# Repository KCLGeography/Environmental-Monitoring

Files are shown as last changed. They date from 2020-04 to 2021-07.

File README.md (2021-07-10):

[][cc-by]

# Environmental-Monitoring
This repo contains the open-source environmental monitoring hardware designs detailed in our *Low-cost electronic sensors for environmental research: pitfalls and opportunities* paper. Designs are included in their individual folders:  
**1. [Basic versatile logger](https://github.com/KCLGeography/environmental-monitoring/tree/master/basic-logger)**  
**2. [Water table depth probe](https://github.com/KCLGeography/environmental-monitoring/tree/master/depth-probe)**  
**3. [Air quality logger](https://github.com/KCLGeography/environmental-monitoring/tree/master/air-quality)**  
**4. [Water quality logger](https://github.com/KCLGeography/environmental-monitoring/tree/master/water-quality)**  
**5. [Time-sequencing lake sediment trap](https://github.com/KCLGeography/environmental-monitoring/blob/master/lake-sediment)**  
**6. [High-frequency measurements of wind-blown sand](https://github.com/KCLGeography/environmental-monitoring/tree/master/Aeolean-sediment-measurer)**  

Schematics and build instructions for the **Freestation Automated Weather Stations** and other specific designs can be found at [www.freestation.org](http://www.freestation.org)

# License
This work is licensed under a [Creative Commons Attribution 4.0 International
License][cc-by] - any use of any material here requires attribution.

### Citation Information:
Chan, K., Schillereff, D., Baas, A., Chadwick, M., Main, B., Mulligan, M., O'Shea, F., Pearce, R., Smith, T.E., van Soesbergen, A., Tebbs, E. and Thompson, J., 2021. Low-cost electronic sensors for environmental research: pitfalls and opportunities. <em>Progress in Physical Geography: Earth and Environment</em> 45(3): 305-338. **[DOI:10.1177/0309133320956567](https://doi.org/10.1177/0309133320956567)**

[][cc-by]

[cc-by]: http://creativecommons.org/licenses/by/4.0/
[cc-by-image]: https://i.creativecommons.org/l/by/4.0/88x31.png
[cc-by-shield]: https://img.shields.io/badge/License-CC%20BY%204.0-lightgrey.svg

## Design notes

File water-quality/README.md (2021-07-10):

[][cc-by]

# Water Quality Logger
Open-source hardware design for the aquatic water quality logger.

## Instructions:
1. Read and confirm the declaration and license associated with these instructions.
2. Start by following the instructions to build and test the [Basic core logger page](https://github.com/KCLGeography/environmental-monitoring/tree/master/basic-logger).

### Adding the DO probe
3. Connect the wires connecting the Atlas Scientific DO probe (complete wiring diagram below).
4. Download the [example code for the Atlas Scientific DO probe](https://www.atlas-scientific.com/_files/code/ino_files/Arduino_UNO_DO_sample_code.zip).
5. Define rx and tx to be 7 and 8 respectively.
6. Upload the file and open the Serial Monitor.
7. Follow the [instructions here](https://www.instructables.com/id/Atlas-Scientific-EZO-DO-Calibration-Procedure/) to calibrate the DO probe.

### Adding the remaining sensors
8. Connect the remaining sensors, including the 5V supply circuitry.
9. Upload the [WaterQualityLogger.ino sketch](WaterQualityLogger.ino).
10. Wait for the reading to occur (every minute) and check that readings are valid in the serial monitor. Results will be in CSV format of Year, month, day, hour, minute, Conductivity voltage, calibrated conductivity (ms/cm), pressure voltage, calibrated temperature (°C), Dissolved Oxygen reading (mg/L).

### Calibrating the EC probe
11. Download and install the [DFRobot_EC Arduino Library](https://github.com/DFRobot/DFRobot_EC/archive/master.zip) within your Arduino IDE.
12. Upload the [ECProbeCalibration.ino](ECProbeCalibration.ino) sketch and follow the calibration instructions [here](https://wiki.dfrobot.com/Gravity__Analog_Electrical_Conductivity_Sensor___Meter_V2__K%3D1__SKU_DFR0300#target_3) noting that you should be using the amended calibration sketch you have already installed, and changing the Serial baud rate to 9600.

### Preparing the final sketch
13. Back in the [WaterQualityLogger.ino sketch](WaterQualityLogger.ino), set the "sleep_period" to a desirable time and reupload the sketch (note, the maximum period without more significant amendment to the sketch is 59 minutes).
14. Test that the logger is working properly before deploying.  

## Wiring diagram (adapted from Fritzing diagram)
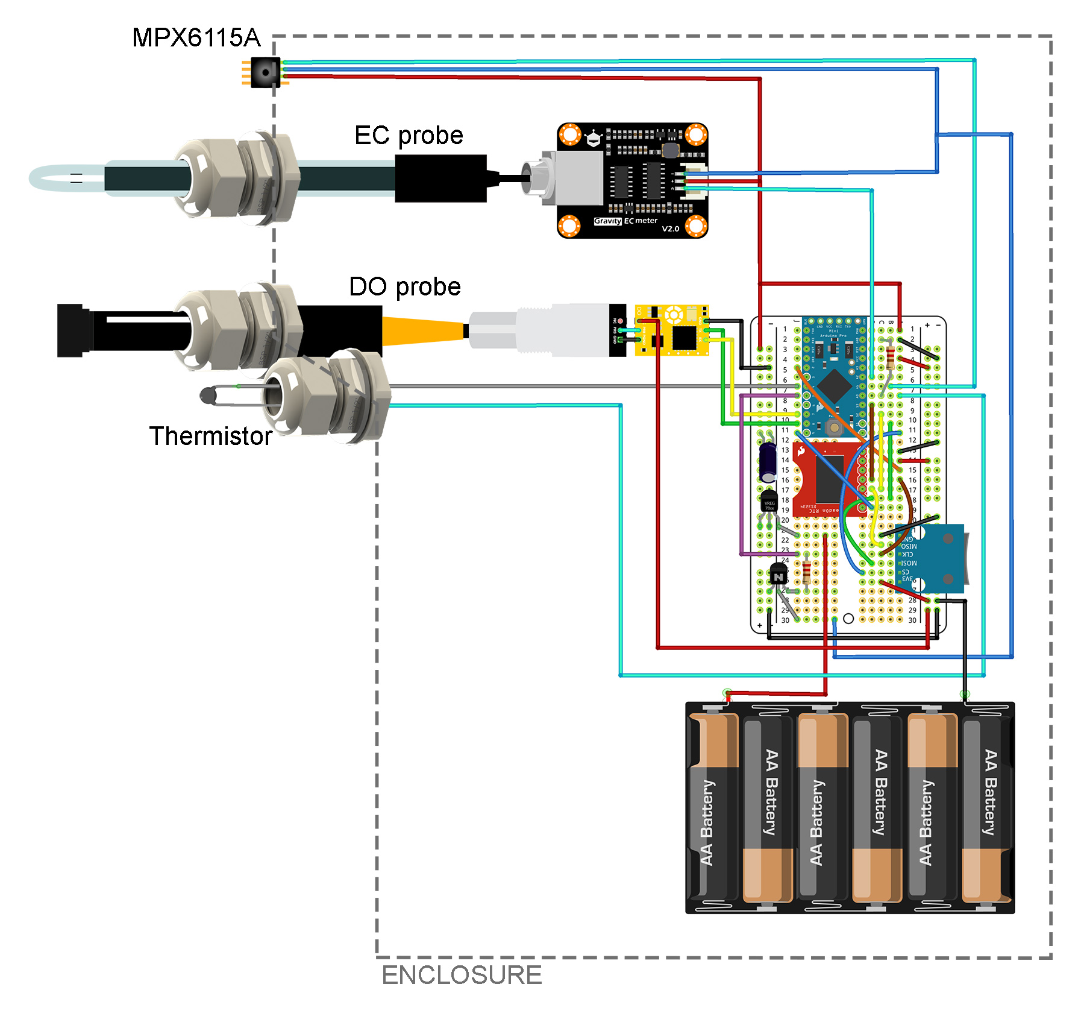
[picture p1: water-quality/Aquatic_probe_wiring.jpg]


## Disclaimer: 
The material in this repository is intended as documentation of the process by which the King's College London environmental monitoring team build our open-source loggers. Though we take care to ensure that the pages are accurate as of the date of publication, Arduino software, libraries, electronic components and interface devices are all subject to variation, change with time, and all introduce the potential for risk. The authors take no responsibility for the consequences of error or for any loss, damage or injury suffered by users or their property as a result of any of the information published on any of these pages, and such information does not form any basis of a contract with readers or users of it. The audience should verify any information provided and only proceed if they have an adequate understanding of electronics and electronics safety.

# License
This work is licensed under a [Creative Commons Attribution 4.0 International
License][cc-by] - any use of any material here requires attribution.

### Citation Information:
Chan, K., Schillereff, D., Baas, A., Chadwick, M., Main, B., Mulligan, M., O'Shea, F., Pearce, R., Smith, T.E., van Soesbergen, A., Tebbs, E. and Thompson, J., 2020. Low-cost electronic sensors for environmental research: pitfalls and opportunities. <em>Progress in Physical Geography: Earth and Environment</em> 45(3): 305-338. **[DOI:10.1177/0309133320956567](https://doi.org/10.1177/0309133320956567)**

[][cc-by]

[cc-by]: http://creativecommons.org/licenses/by/4.0/
[cc-by-image]: https://i.creativecommons.org/l/by/4.0/88x31.png
[cc-by-shield]: https://img.shields.io/badge/License-CC%20BY%204.0-lightgrey.svg

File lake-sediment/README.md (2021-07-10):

[][cc-by]

# Time-sequencing lake sediment traps
Open-source hardware design for time-sequencing lake sediment traps. in our design, the carousel rotates every month and exposes a new sediment trap, which collects sediment in the water column. 

## Instructions:
1. Read and confirm the declaration and license associated with these instructions.
2. Ensure you have purchased all the necessary parts listed in the [Bill of Materials sheet](https://docs.google.com/spreadsheets/d/1BAKtbqieHCemCTPPsL36uj2QXcKh0NGoTecxeYXc90M/edit#gid=1020050693).
3. In this design, we solder screw terminals to the components for more robust deployment, though direct soldering onto the components would be more secure. You can also adapt the instructions to using a breadboard. Start by assembling the basic logger by assembling the wiring diagram of the basic logger below.
4. Follow the test instructions on the [Basic core logger page](https://github.com/KCLGeography/environmental-monitoring/tree/master/basic-logger) to set and test the clock and microSD card communication.
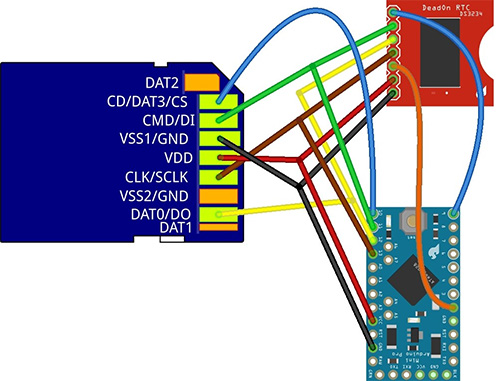
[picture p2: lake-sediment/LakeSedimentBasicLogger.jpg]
Soldered Basic Logger schematic (made with Fritzing)


### Adding the Relay
5. Add the Relay and communication ports for the stepper motor following the assembly diagram below or included in this folder: [LakeSedimentRelay.jpg](LakeSedimentRelay.jpg).
6. Upload the [LakeSedimentTrap sketch](LakeSedimentTrap.ino).
7. The stepper motor should rotate and the relay should click on/off. Though we could run the stepper without direct powering (i.e. without the need for the relay), it is more stable to run with this.
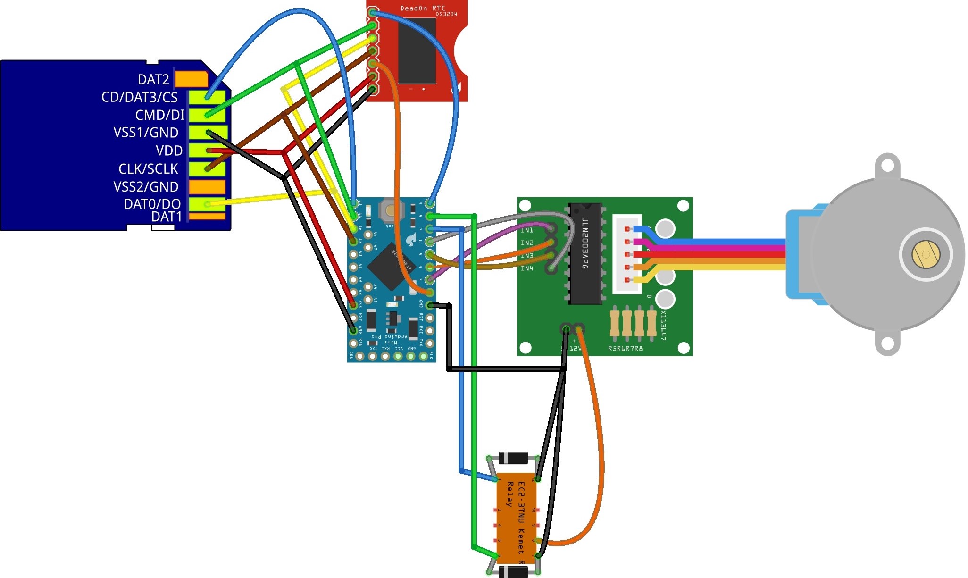
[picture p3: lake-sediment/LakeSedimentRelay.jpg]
Stepper and relay circuit schematic (made with Fritzing)


### Connecting the power pack
8. Connect the battery pack (6xAA recommended for annual deployment) following the wiring diagram below and test that the circuit still works.
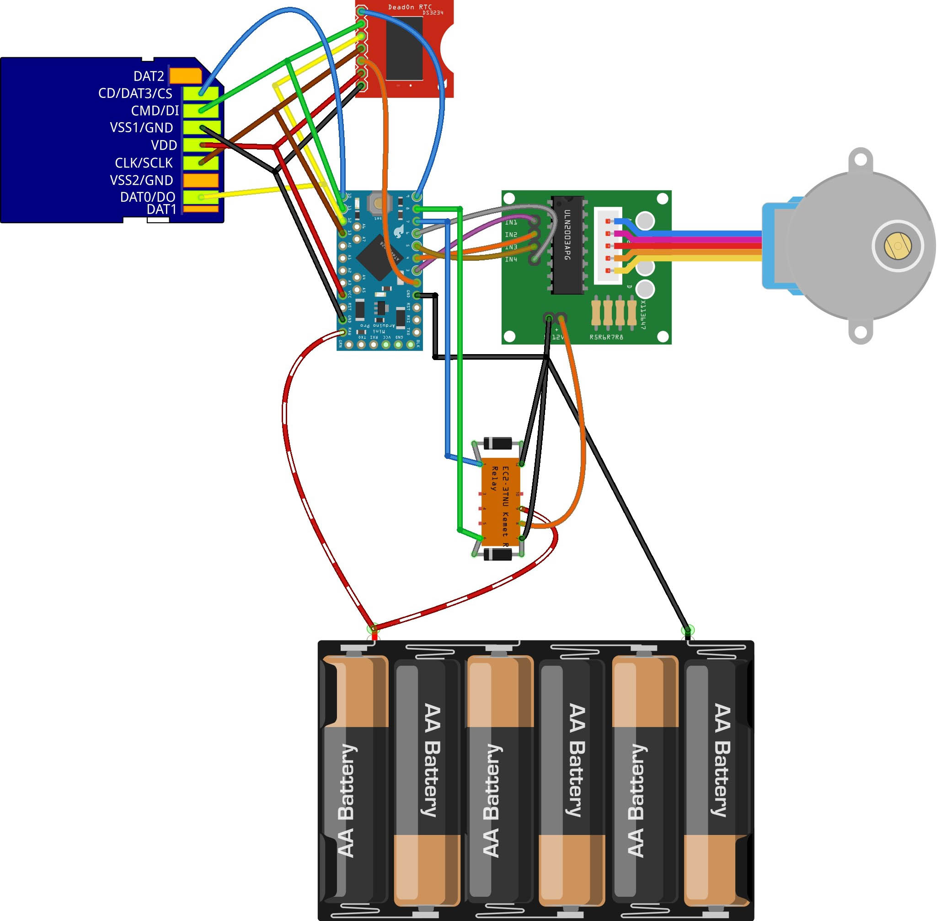
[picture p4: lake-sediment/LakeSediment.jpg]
Full circuit schematic (made with Fritzing)


## Assembling the hardware
Disconnect a battery whilst the below is prepared.

### Preparing the enclosure
9. Drill a 13mm hole in the center of a quadrant of the bottom of the enclosure. This is for the the cable gland and where the axle will pass through. Ensure that burrs on the edges are removed.
10. Check the fitting of the stepper, stepper mechanism and axle. If they fit together well, epoxy these together.
11. Mount the cable gland to the bottom of the enclosure and position the stepper motor in the correct position over the cable gland. Using epoxy, glue the mounting brackets for the stepper motor to the base of the enclosure. Also glue the enclosure to the top of the sediment trap cover.

### Preparing the carousel
12. Drill holes in the tops of 12 of the sampling bottles, being careful to remove and burrs.
13. With epoxy, glue the lids of the sampling bottles into the carousel.

### Preparing the trap top
14. Cut the filter such that it fits into the 4" pipe snugly.
15. Position the foam camping matt against the lake sediment trap top cover and cut around the trap cover. Mark and cut a small hole where the axle and filter will go through the piece - the holes should accommodate the axle and filter bottom snugly. 
16. Epoxy the prepared camping matt to the sediment trap top.
17. Cut the pipe to a length of 75cm.
18. Using epoxy, glue the filter and pipe to the top cover of the lake sediment trap. Wait for this to dry.
19. Put some silicon grease along the section of axle which will rotate within the gland.
20. Push the stepper and axle through the enclosure and mount the stepper motor to the brackets with nuts and bolts. Glue the axle as far through the sediment trap top as it will go whilst still mounted to the stepper in the correct position. The top of the carousel should be snug against the foam.
21. Wait for this to dry then test that it still works.

### Waterproofing
22. Apply silicon grease to the lid of the enclosure for waterproofing. 
23. With the stepper motor disconnected and all components except the stepper absent, close the enclosure and verify the waterproofing of the enclosure in a sink, bathtub or bucket.
24. Test that the circuit still works as expected before commenting out the minutely test code section in the set alarm subroutine and commenting in the deployment code. Flash the deployment version of the software to the Arduino.
25. You may want to melt and pour candle wax into the enclosure to encase the logger components to improve waterproofing if deploying at greater depths (>3m); if opting to do this, ensure you have enough space for the batteries.

### Final preparations
26. Reconnect the stepper, connect the batteries and place all the components inside and close the enclosure.
27. Mount the sediment trap such that the pipe is vertical in the water column. Refer to our article for more specific mounting information.

## Disclaimer: 
The material in this repository is intended as documentation of the process by which the King's College London environmental monitoring team build our open-source loggers. Though we take care to ensure that the pages are accurate as of the date of publication, Arduino software, libraries, electronic components and interface devices are all subject to variation, change with time, and all introduce the potential for risk. The authors take no responsibility for the consequences of error or for any loss, damage or injury suffered by users or their property as a result of any of the information published on any of these pages, and such information does not form any basis of a contract with readers or users of it. The audience should verify any information provided and only proceed if they have an adequate understanding of electronics and electronics safety.

# License
This work is licensed under a [Creative Commons Attribution 4.0 International
License][cc-by] - any use of any material here requires attribution.

### Citation Information:
Chan, K., Schillereff, D., Baas, A., Chadwick, M., Main, B., Mulligan, M., O'Shea, F., Pearce, R., Smith, T.E., van Soesbergen, A., Tebbs, E. and Thompson, J., 2020. Low-cost electronic sensors for environmental research: pitfalls and opportunities. <em>Progress in Physical Geography: Earth and Environment</em> 45(3): 305-338. **[DOI:10.1177/0309133320956567](https://doi.org/10.1177/0309133320956567)**

[][cc-by]

[cc-by]: http://creativecommons.org/licenses/by/4.0/
[cc-by-image]: https://i.creativecommons.org/l/by/4.0/88x31.png
[cc-by-shield]: https://img.shields.io/badge/License-CC%20BY%204.0-lightgrey.svg

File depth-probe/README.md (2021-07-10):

[][cc-by]

# Depth Probe Logger
Open-source hardware design for Water table depth probe logger.

# Instructions
1. Ensure you have read and understand the disclaimer and license associated with this guide.
2. Acquire the necessary parts listed in the [Bill of Materials](https://docs.google.com/spreadsheets/d/1BAKtbqieHCemCTPPsL36uj2QXcKh0NGoTecxeYXc90M/edit#gid=1699271503).
3. With the exception of the Li-ion battery, assemble the circuitry following the hookup schematic below or included in this folder [Depth-probe.png](Depth-probe.png) and [Depth-probe-schematic.jpg](Depth-probe-schematic.jpg). 
4. Taking take to ensure you are connecting the programmer correctly. Follow the steps to set/test the DS3234 clock and microSD card module from the [Basic core logger page](https://github.com/KCLGeography/environmental-monitoring/tree/master/basic-logger).
5. If successful, download and install [Luke Miller's MS5803 (2-bar) library](http://github.com/millerlp/MS5803_02).
6. Upload the [Depth-logger.ino](Depth-logger.ino) sketch to the 3.3V Pro Mini and check that the MS5803 is outputting expected results.
7. Drill a 6.5mm hole in the end-cap of the enclosure. Clean after drilling.
8. Cut a 4cm length of the hose and slide it around the round metal casing of the MS5803.
9. Begin pushing the open end of the hose through the hole in the end-cap so that ~1cm is protuding through the end.
10. Apply epoxy resin inside the end-cap.
11. Push the MS5803 and hose to the end of the end-cap. Apply epoxy generously to the rear of the MS5803 (this is what will hold the MS5803 in place against the water pressure!).
12. Let the epoxy set then retest to make sure the setup is still working.
13. **Li-ion batteries are potentially dangerous. If you do not have the skills, qualifications or experience to conduct the next step, we would advise seeking assistance from those who do.** Solder or spot-weld the 18650 battery to the setup.
14. Connect the TP4056 charger and charge the Li-ion battery. Disconnect once fully charged.
15. If successful, gently position the logger components into the tubing.
16. Apply plumbing tape to the threads and close the enclosure. Test against a reliable depth logger or against known depths to check for accuracy.

### Hook-up diagram (made with Fritzing):
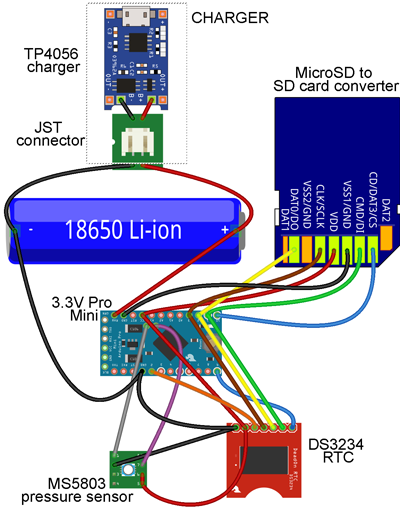
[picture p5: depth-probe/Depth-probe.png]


### Circuit schematic (made with Fritzing):
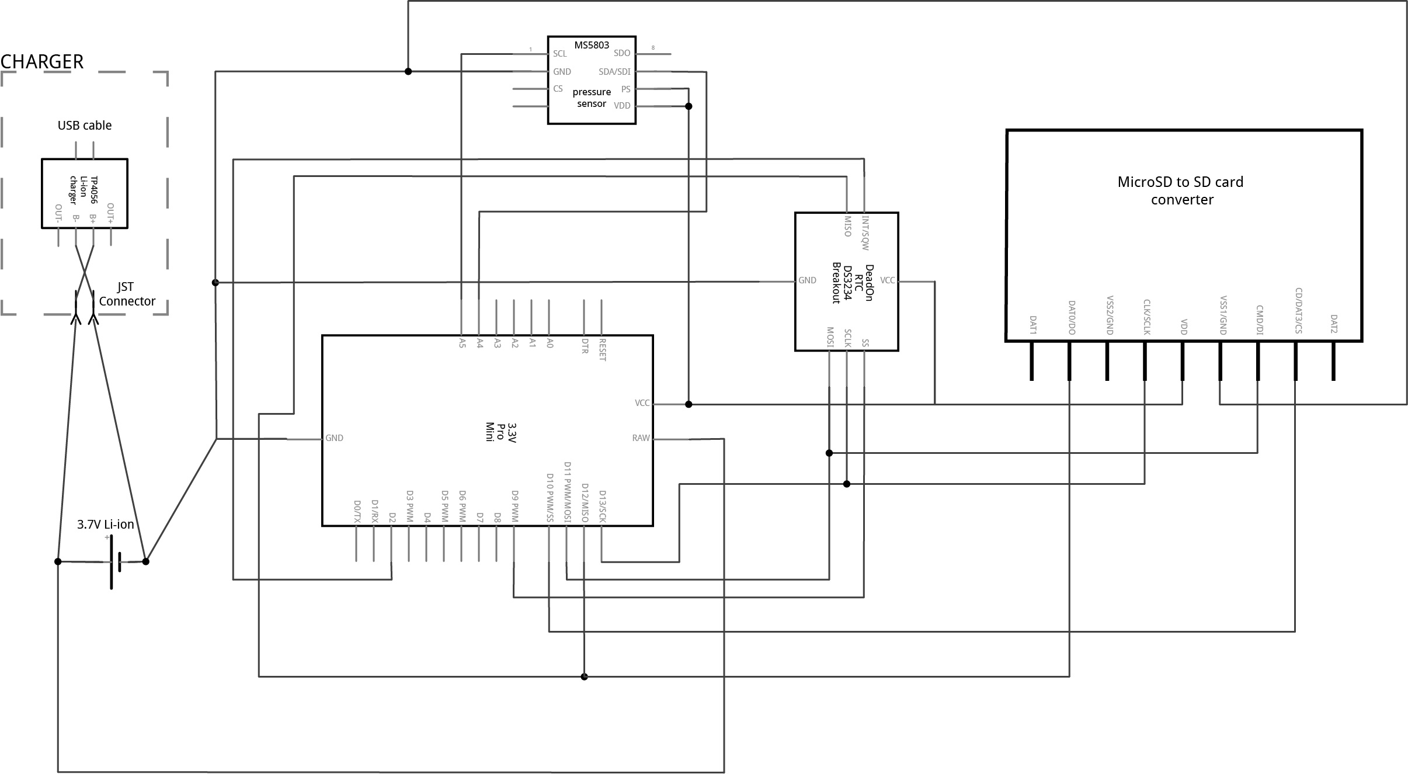
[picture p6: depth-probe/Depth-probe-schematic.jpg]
Hook-up schematic (made with Fritzing)


### Disclaimer: 
The material in this repository is intended as documentation of the process by which the King's College London environmental monitoring team build our open-source loggers. Though we take care to ensure that the pages are accurate as of the date of publication, Arduino software, libraries, electronic components and interface devices are all subject to variation, change with time, and all introduce the potential for risk. The authors take no responsibility for the consequences of error or for any loss, damage or injury suffered by users or their property as a result of any of the information published on any of these pages, and such information does not form any basis of a contract with readers or users of it. The audience should verify any information provided and only proceed if they have an adequate understanding of electronics and electronics safety.

# License
This work is licensed under a [Creative Commons Attribution 4.0 International
License][cc-by] - any use of any material here requires attribution.

### Citation Information:
Chan, K., Schillereff, D., Baas, A., Chadwick, M., Main, B., Mulligan, M., O'Shea, F., Pearce, R., Smith, T.E., van Soesbergen, A., Tebbs, E. and Thompson, J., 2020. Low-cost electronic sensors for environmental research: pitfalls and opportunities. <em>Progress in Physical Geography: Earth and Environment</em> 45(3): 305-338. **[DOI:10.1177/0309133320956567](https://doi.org/10.1177/0309133320956567)**

[][cc-by]

[cc-by]: http://creativecommons.org/licenses/by/4.0/
[cc-by-image]: https://i.creativecommons.org/l/by/4.0/88x31.png
[cc-by-shield]: https://img.shields.io/badge/License-CC%20BY%204.0-lightgrey.svg

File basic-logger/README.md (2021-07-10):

[][cc-by]

## Instructions
1. Read and confirm the disclaimer (bottom of this page) and CC-BY license usage (main repository).
2. Source the material listed in the [Bill-Of-Materials document](https://docs.google.com/spreadsheets/d/1BAKtbqieHCemCTPPsL36uj2QXcKh0NGoTecxeYXc90M).
3. Connect the logger as shown in the breadboard connection diagram (basic-logger-breadboard.jpg file or shown below). Take care to ensure you connect the battery terminals correctly and make sure you do not leave loose wires trailing (with the potential for short-circuiting).
4. Remove the battery pack from the circuit whenever plugging the Arduino into your computer (taking the necessary precautions).
5. Ensure the DS3234 clock has the correct battery in the correct way around.
6. Ensure the microSD card holder has a suitable microSD card with a suitable formatting (FAT32 or <2GB FAT16 micro SD).
7. Connect the 3.3V Pro Mini to your computer using a suitable programmer.
8. Set the correct Arduino (3.3V pro mini) and COM port which the device is connected to.
#### Clock setup and testing
9. Download and install the [DS3234 library](https://github.com/rodan/ds3234) to your Arduino IDE.
10. Set the Chip Select value to 9 (i.e. change "const int cs = 10;" to "const int cs = 9;") 
11. Find the rtc_ds3234 example (File>Example>DS3234>rtc_ds3234) sketch and flash it to the Pro Mini.
12. Open the serial monitor and ensure the baud rate is set at '9600 baud' and line ending is set to 'Both NL & CR'). If connected correctly, your clock should be showing an incrementally increasing time every 5 seconds; if it is not, disconnect the programmer from your computer, recheck the wiring and restart the process.
13. In the input window, set the time following the format TssmmhhWDDMMYYYY and hit Enter (E.g. T001122501052020 for 22:11:00 on Friday 1st May 2020).
14. plug your Arduino back into your computer and reopen the Serial monitor (you may need to make sure the correct COM port is set under Tools > Port). Your clock should be maintaining and Serial printing the time without the need for resetting.

#### SD card setup and testing
15. Download and install the [SDFat library](https://github.com/greiman/SdFat) to your Arduino IDE.
16. Find the QuickStart example (File>Example>SdFat>Quickstart) and flash this to the Pro Mini.
17. Open the serial monitor (ensuring settings are '9600 baud' and 'both NL & CR').
18. Type 10 then hit Enter.
19. The Pro Mini should reply with a "Card successfully initialized." message. If not, disconnect the Pro Mini from your computer, recheck the wiring and that the microSD card is formatted correctly and inserted the correct way.

### Pro Mini Temperature Logger sketch
At this point, you have successfully tested the individual components. We can now upload a basic temperature logger sketch, which takes the temperature from the DS3234 RTC (calibrated) and an uncalibrated temperature measurement from the ATMega328p processor and writes them to the microSD card and serial.
1. Download the [basic logger test sketch](BasicLogger.ino) and flash it to your Arduino.
2. Open the Serial Monitor and observe the results.
3. Unplug the Arduino and check the data has been successfully written to the CSV file on the microSD card. Columns will be formatted:
Year, Month, Date, Hour, Minute, ATmega328 temp, DS3234 temp
4. The sketch acts as a skeleton upon which can very quickly be adapted for the measurement and logging of other sensors.

### Basic logger breadboard connection diagram (image made with Fritzing):

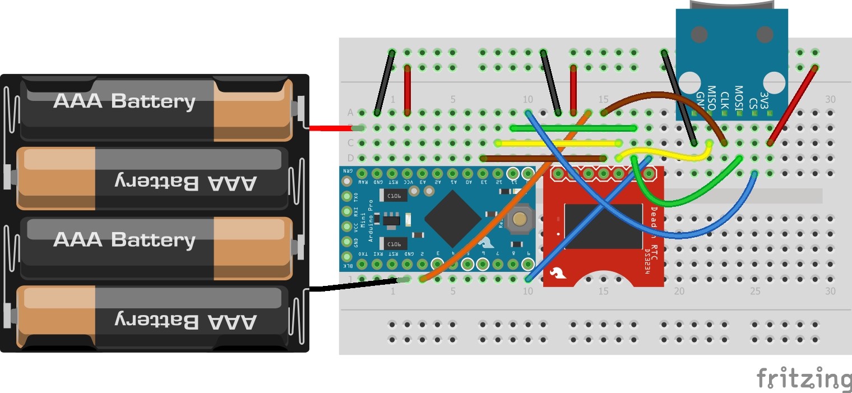
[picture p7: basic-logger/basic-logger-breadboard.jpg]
Basic logger breadboard connection diagram
  

Note that the wires are coloured with the following colouration:  
Red - +ve power terminal (from battery or VCC/3.3V)  
Black - GND  
Blue - CS/SS  
Green - MOSI  
Yellow - MISO  
Brown - CLK  
Orange - SQW/INT  

### Basic logger breadboard circuit schematics (image made with Fritzing):

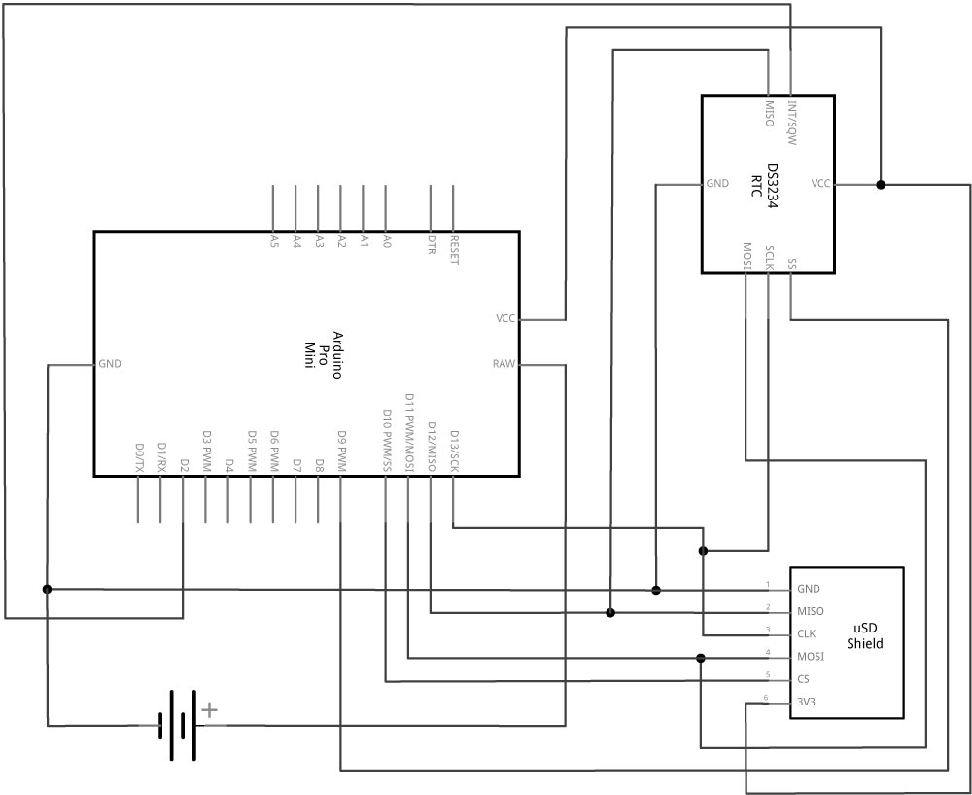
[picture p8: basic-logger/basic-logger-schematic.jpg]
Basic


### Disclaimer: 
The material in this repository is intended as documentation of the process by which the King's College London environmental monitoring team build our open-source loggers. Though we take care to ensure that the pages are accurate as of the date of publication, Arduino software, libraries, electronic components and interface devices are all subject to variation, change with time, and all introduce the potential for risk. The authors take no responsibility for the consequences of error or for any loss, damage or injury suffered by users or their property as a result of any of the information published on any of these pages, and such information does not form any basis of a contract with readers or users of it. The audience should verify any information provided and only proceed if they have an adequate understanding of electronics and electronics safety.

# License
This work is licensed under a [Creative Commons Attribution 4.0 International
License][cc-by] - any use of any material here requires attribution.

### Citation Information:
Chan, K., Schillereff, D., Baas, A., Chadwick, M., Main, B., Mulligan, M., O'Shea, F., Pearce, R., Smith, T.E., van Soesbergen, A., Tebbs, E. and Thompson, J., 2020. Low-cost electronic sensors for environmental research: pitfalls and opportunities. <em>Progress in Physical Geography: Earth and Environment</em> 45(3): 305-338. **[DOI:10.1177/0309133320956567](https://doi.org/10.1177/0309133320956567)**

[][cc-by]

[cc-by]: http://creativecommons.org/licenses/by/4.0/
[cc-by-image]: https://i.creativecommons.org/l/by/4.0/88x31.png
[cc-by-shield]: https://img.shields.io/badge/License-CC%20BY%204.0-lightgrey.svg

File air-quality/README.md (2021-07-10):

[][cc-by]

# Air Quality Logger
Open-source hardware design for air quality logger measuring particulate matter (PM10, PM2.5, PM1), chemical air quality (NO2, NO, O3) and temperature, relative humidity and barometric pressure.

## Instructions:
1. Read and confirm the declaration and license associated with these instructions.
2. Ensure you have purchased all the necessary parts listed in the [Bill of Materials sheet](https://docs.google.com/spreadsheets/d/1BAKtbqieHCemCTPPsL36uj2QXcKh0NGoTecxeYXc90M/edit#gid=558654440).
3. Start by following the instructions to build and test the [Basic core logger page](https://github.com/KCLGeography/environmental-monitoring/tree/master/basic-logger).

### Adding the BME280
4. Add the BME280 following the assembly diagram below or included in this folder: [BME280.jpg](BME280.jpg).
5. Follow the instructions under 'Install Adafruit_BME280 library' [here] (https://learn.adafruit.com/adafruit-bme280-humidity-barometric-pressure-temperature-sensor-breakout/arduino-test#install-adafruit-bme280-library-2958101-7) to test the BME280, ensuring you have the board set to "Arduino Pro or Pro Mini", processor set to "ATmega328P (3.3V, 8MHz)" and port which you have connected your programmer to (both under the Tools menu). **Note** should the device not work, your BME280 may be on a non-standard address (i.e. not 0x77). You can check it's address by uploading and running [the i2c scanner] (https://playground.arduino.cc/Main/I2cScanner/). Should the address not be the standard, you can change this within the Adafruit BME280 library files (within .../My Documents/Arduino/libraries/Adafruit_BME280_Library/Adafruit_BME280.h)
6. If working, move to the next section.
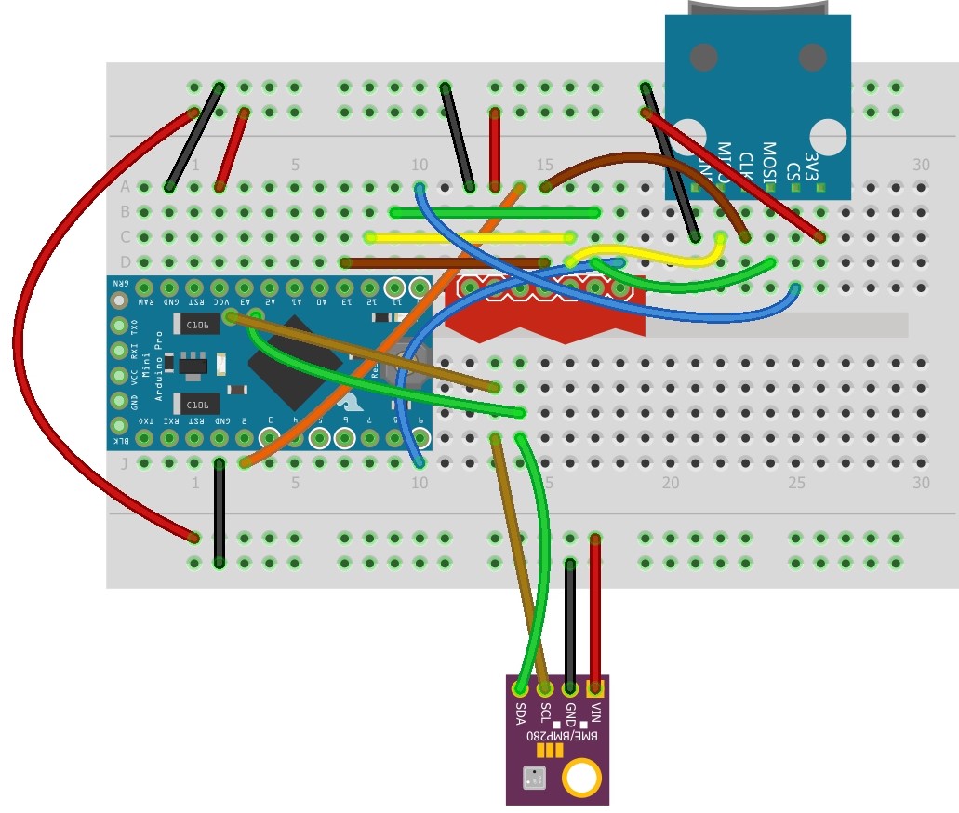
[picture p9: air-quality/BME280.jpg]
BME280 addition schematic (made with Fritzing)


### Adding the PM sensor
7. Add the Pololu step-up voltage regulator and the PMS-5003 following the assembly diagram below or included in this folder: [Plantower.jpg](Plantower.jpg).
8. Upload the [Only_PM.ino](Only_PM.ino) sketch to the Pro Mini and check the serial monitor (results should be displayed and written to the microSD card every minute).
9. The sensor is now a functioning PM logger.
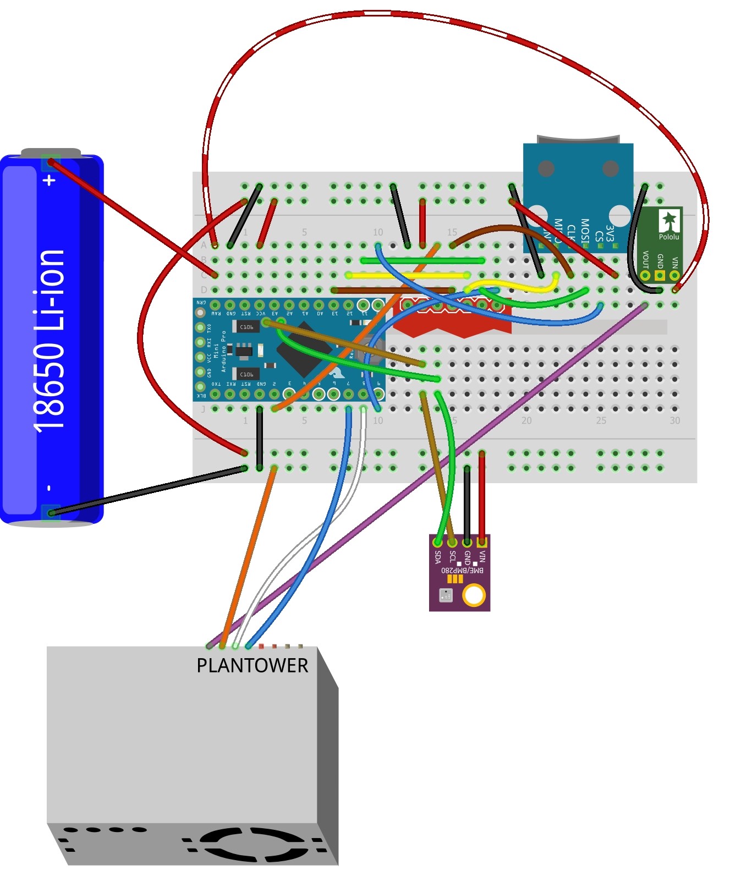
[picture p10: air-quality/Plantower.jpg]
Plantower addition schematic (made with Fritzing)


### Adding the Alphasense chemical air quality sensors
10.  Add the ADS1115 ADCs and the Alphasense Analogue Front End following the assembly diagram below or included in this folder: [Air-quality-diagram.jpg](Air-quality-diagram.jpg). Note: we include a [labelled version without wires](AirQuality-NoWires-Labelled.jpg) should you have trouble identifying parts or pin locations.
11. Upload the [NOx_PM.ino](NOx_PM.ino) sketch to the Pro Mini and check the serial monitor (results should be displayed and written to the microSD card every minute).
12. Set the appropriate sleep times and a suitable filename for your data. Remember to check before deployment.
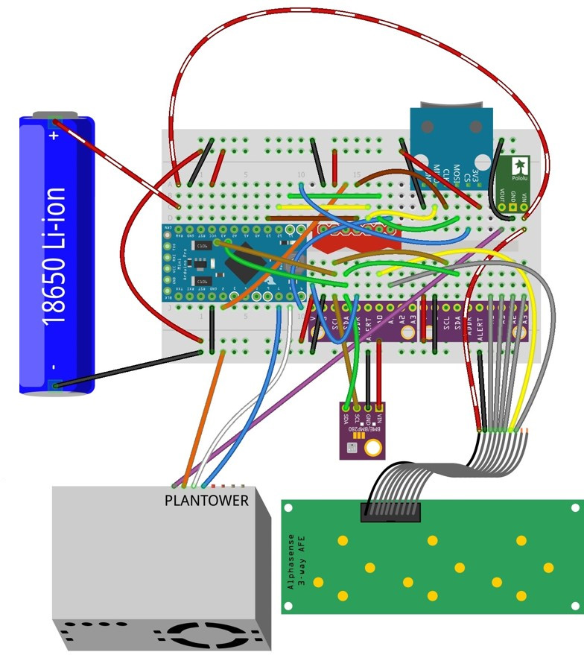
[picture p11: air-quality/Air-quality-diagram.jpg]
Complete air quality logger schematic (made with Fritzing)


### Disclaimer: 
The material in this repository is intended as documentation of the process by which the King's College London environmental monitoring team build our open-source loggers. Though we take care to ensure that the pages are accurate as of the date of publication, Arduino software, libraries, electronic components and interface devices are all subject to variation, change with time, and all introduce the potential for risk. The authors take no responsibility for the consequences of error or for any loss, damage or injury suffered by users or their property as a result of any of the information published on any of these pages, and such information does not form any basis of a contract with readers or users of it. The audience should verify any information provided and only proceed if they have an adequate understanding of electronics and electronics safety.

# License
This work is licensed under a [Creative Commons Attribution 4.0 International
License][cc-by] - any use of any material here requires attribution.

### Citation Information:
Chan, K., Schillereff, D., Baas, A., Chadwick, M., Main, B., Mulligan, M., O'Shea, F., Pearce, R., Smith, T.E., van Soesbergen, A., Tebbs, E. and Thompson, J., 2020. Low-cost electronic sensors for environmental research: pitfalls and opportunities. <em>Progress in Physical Geography: Earth and Environment</em> 45(3): 305-338. **[DOI:10.1177/0309133320956567](https://doi.org/10.1177/0309133320956567)**

[][cc-by]

[cc-by]: http://creativecommons.org/licenses/by/4.0/
[cc-by-image]: https://i.creativecommons.org/l/by/4.0/88x31.png
[cc-by-shield]: https://img.shields.io/badge/License-CC%20BY%204.0-lightgrey.svg

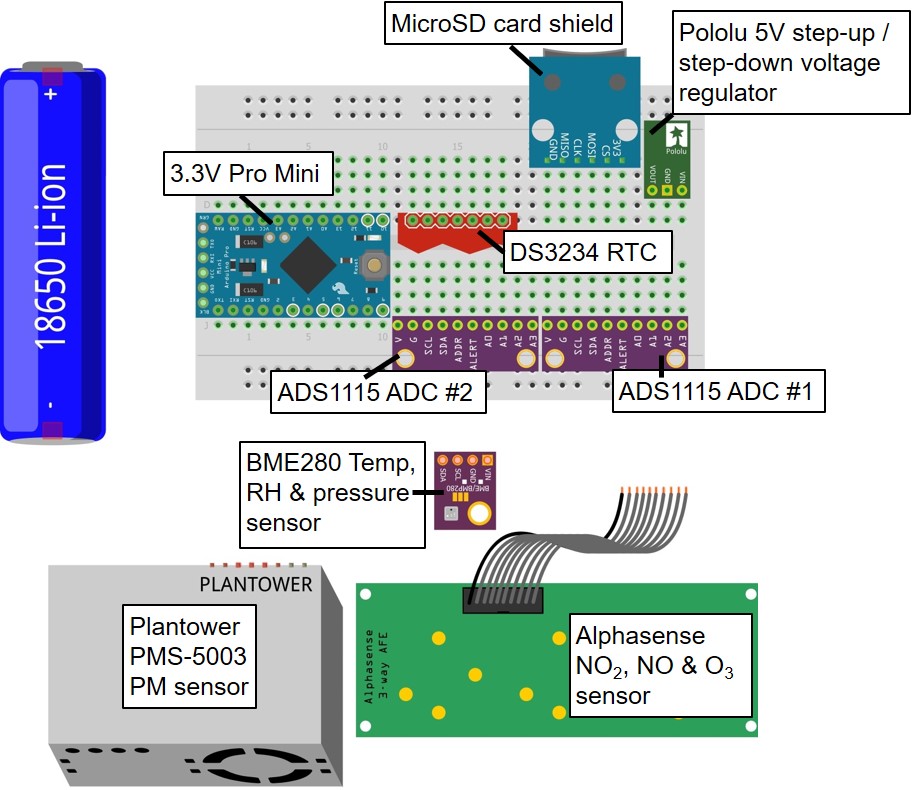
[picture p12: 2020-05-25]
air-quality/AirQuality-NoWires-Labelled.jpg

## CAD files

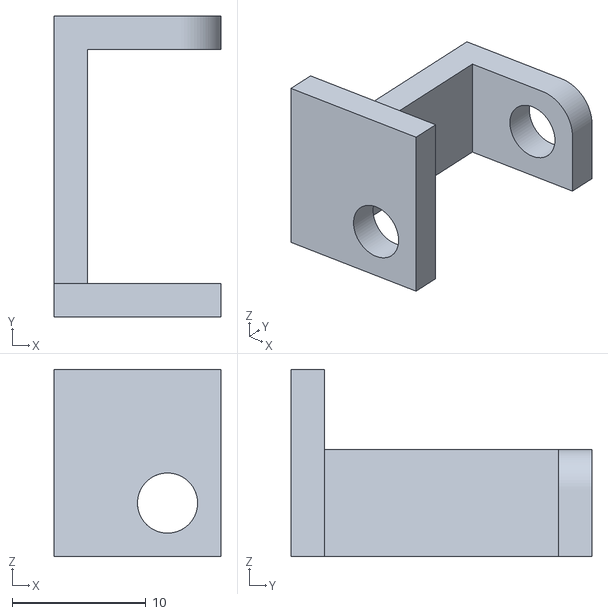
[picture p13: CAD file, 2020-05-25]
lake-sediment/stepperbracket.stl
12.5 x 22.5 x 14.0

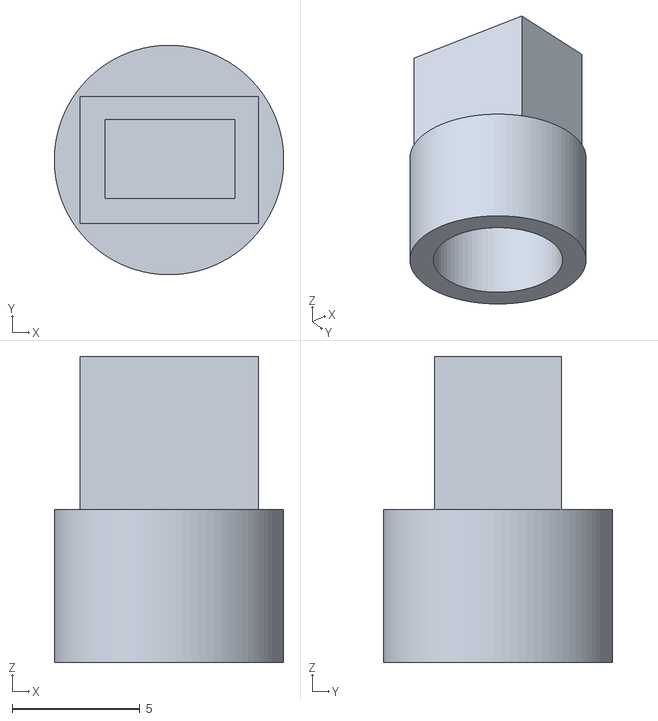
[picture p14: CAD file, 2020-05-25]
lake-sediment/StepperAttachment.stl
9.00 x 9.00 x 12.0

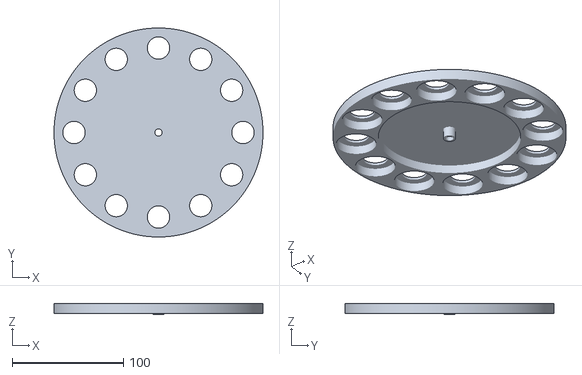
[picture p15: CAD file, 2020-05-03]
lake-sediment/Trap_carousel.stl
188.0 x 188.0 x 10.0

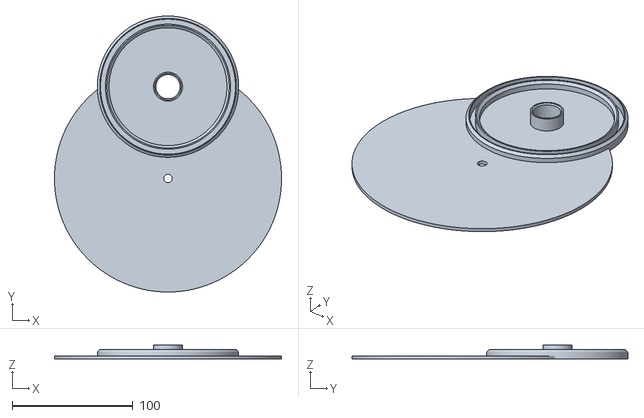
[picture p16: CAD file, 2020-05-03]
lake-sediment/Trap_top.stl
188.0 x 228.5 x 12.0

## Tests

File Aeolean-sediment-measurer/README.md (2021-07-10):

[][cc-by]

# Aeolean Sediment Measurer
Open-source hardware design for High-frequency measurement of wind-blown sand.

# Instructions
1. Ensure you have read and understand the disclaimer and license associated with this guide.
2. Acquire the necessary parts listed in the [Bill of Materials](https://docs.google.com/spreadsheets/d/1BAKtbqieHCemCTPPsL36uj2QXcKh0NGoTecxeYXc90M/edit#gid=590094508).
3. Assemble the circuitry following the hookup schematic below or included in this folder [SonicandWenglor.jpg](SonicandWenglor.jpg).
4. Upload the sketch to the Arduino Duo.

### Hook-up schematic (made with Fritzing):
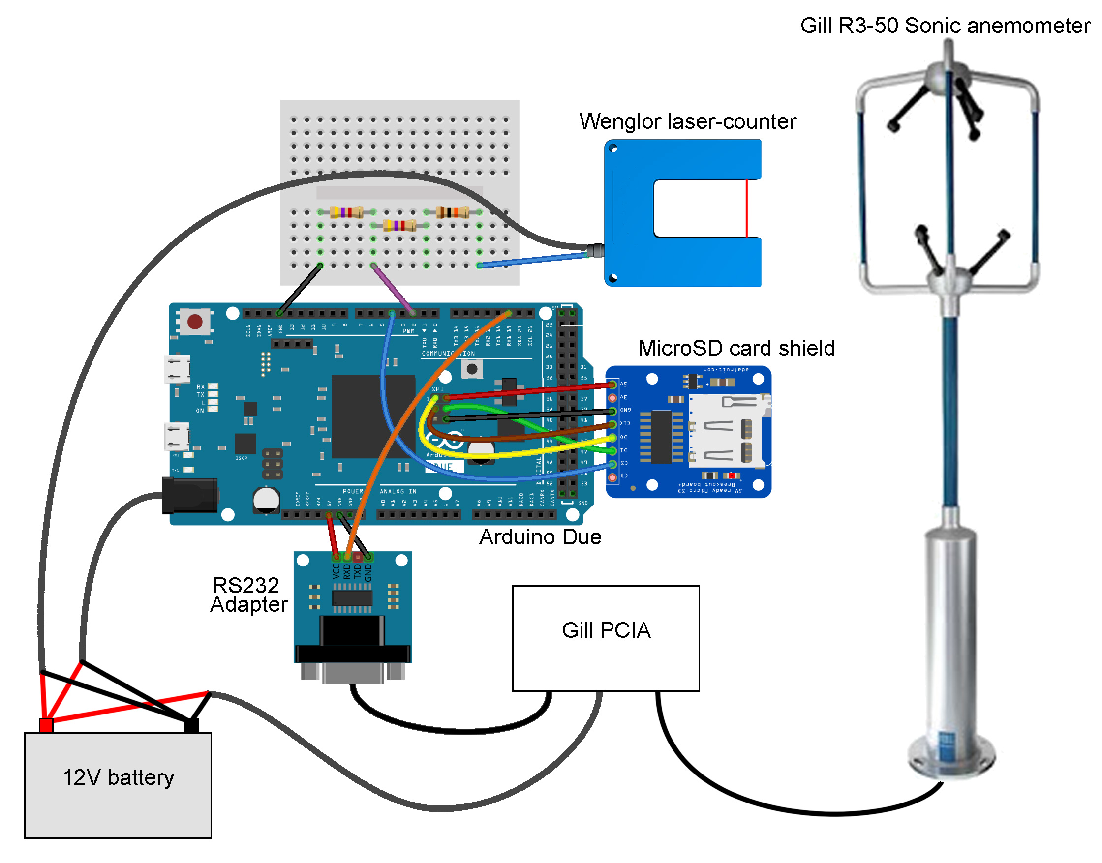
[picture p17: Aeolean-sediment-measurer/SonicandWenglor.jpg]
Hook-up schematic (made with Fritzing)


### Disclaimer: 
The material in this repository is intended as documentation of the process by which the King's College London environmental monitoring team build our open-source loggers. Though we take care to ensure that the pages are accurate as of the date of publication, Arduino software, libraries, electronic components and interface devices are all subject to variation, change with time, and all introduce the potential for risk. The authors take no responsibility for the consequences of error or for any loss, damage or injury suffered by users or their property as a result of any of the information published on any of these pages, and such information does not form any basis of a contract with readers or users of it. The audience should verify any information provided and only proceed if they have an adequate understanding of electronics and electronics safety.

# License
This work is licensed under a [Creative Commons Attribution 4.0 International
License][cc-by] - any use of any material here requires attribution.

### Citation Information:
Chan, K., Schillereff, D., Baas, A., Chadwick, M., Main, B., Mulligan, M., O'Shea, F., Pearce, R., Smith, T.E., van Soesbergen, A., Tebbs, E. and Thompson, J., 2021. Low-cost electronic sensors for environmental research: pitfalls and opportunities. <em>Progress in Physical Geography: Earth and Environment</em> 45(3): 305-338. **[DOI:10.1177/0309133320956567](https://doi.org/10.1177/0309133320956567)**

[][cc-by]

[cc-by]: http://creativecommons.org/licenses/by/4.0/
[cc-by-image]: https://i.creativecommons.org/l/by/4.0/88x31.png
[cc-by-shield]: https://img.shields.io/badge/License-CC%20BY%204.0-lightgrey.svg

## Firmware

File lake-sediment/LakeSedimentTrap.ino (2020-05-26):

// Code developed by Environmental Research Group, Department of Geography, King's College London //
////////////////////////////////////////////////////////////////////////////////////////////////////

/* LIBRARIES */
#include <SPI.h>                  //SPI Communication library
#include <avr/sleep.h>            //low power library
#include <avr/power.h>            //low power library
#include "ds3234.h"               //DS3234 RTC library. Available from https://github.com/rodan/ds3234
#include <SdFat.h>                //SD card library. Available from https://github.com/greiman/SdFat
#include <Stepper.h>              //Stepper motor library. Installable in Arduino IDE via Sketch>Include Library>Manage Libraries>Search for "Stepper". Version used: 1.1.3

//SD HOUSEKEEPING
  SdFat sd;
  SdFile file;
  char newfile[] = "LakeTemplogger.csv";      //name of file
  const int CS = 10;        //sd card chip select

//RTC & ALARM HOUSEKEEPING
  int ss = 9;               //clock chip select
  int AlarmPin = 2;         //pin which alarm communicates with
  unsigned int wADC;
  // time when to wake up
  uint8_t wake_DAY = 1;
  uint8_t wake_HOUR = 12;
  uint8_t wake_MINUTE = 0;
  uint8_t wake_SECOND = 0;
  struct ts t;

//STEPPER MOTOR HOUSEKEEPING
  //---( Number of steps per revolution of INTERNAL motor in 4-step mode )---
  #define STEPS_PER_MOTOR_REVOLUTION 32   
  
  //---( Steps per OUTPUT SHAFT of gear reduction )---
  #define STEPS_PER_OUTPUT_REVOLUTION 32 * 64  //2048  
  
  //The pin connections need to be 4 pins connected
  // to Motor Driver In1, In2, In3, In4  and then the pins entered
  // here in the sequence 1-3-2-4 for proper sequencing
  Stepper small_stepper(STEPS_PER_MOTOR_REVOLUTION, 3, 5, 4, 6);// 3, 5, 4, 6
  
  /*-----( Declare Variables )-----*/
  int  Steps2Take;
  const int relay_on = 7;
  const int relay_off = 8;


/* ALARM SUBROUTINE. NOTE TEST/DEPLOYMENT OPTIONS BELOW! */
void set_alarm(void){


    //TEST CODE. COMMENT OUT FOR ACTUAL DEPLOYMENT.
    uint8_t flags[5] = { 0, 0, 0, 1, 1 };
    DS3234_set_a1(ss, wake_SECOND, 0, 0, 0, flags);
    DS3234_set_creg(ss, DS3234_INTCN | DS3234_A1IE);

    //DEPLOYMENT CODE. COMMENT IN THE BELOW FOR ACTUAL DEPLOYMENT.
    //uint8_t flags[5] = { 0, 0, 0, 0, 0 };
    //DS3234_set_a1(ss, wake_SECOND, wake_MINUTE, wake_HOUR, wake_DAY, flags);
    //DS3234_set_creg(ss, DS3234_INTCN | DS3234_A1IE);
   
}
 
void setup() {
Serial.begin(9600);
//  Serial.println("setupstart");
  SPI.beginTransaction(SPISettings(6000000, MSBFIRST, SPI_MODE3));
  DS3234_init(ss, DS3234_INTCN);  
  delay(10);
  DS3234_get(ss, &t);
  delay(10);
  DS3234_clear_a1f(ss);
  delay(10);
  set_alarm();
  delay(5);
  pinMode (AlarmPin, INPUT);
  pinMode(relay_on, OUTPUT);
  pinMode(relay_off, OUTPUT);
  
  digitalWrite(relay_off, HIGH);
  delay(50);
  digitalWrite(relay_off, LOW);

  
  attachInterrupt(0, alarm, FALLING); // setting the alarm interrupt 
  delay(100);

 while (!sd.begin(CS, SPI_HALF_SPEED)) {}
  // open the file for write at end like the Native SD library
  file.open(newfile, O_WRITE | O_CREAT | O_APPEND);
  file.close();
Serial.println("setupend"); //would print to the Arduino screen if connected
 delay(100); 
 }


void loop() {
  gotoSleep();              //Arduino put to sleep
  
  Serial.println("loop"); //would print to the Arduino screen if connected
  delay(50);
  GetTemp();
  int InternalTemp = wADC;
//Arduino wakes up here

  digitalWrite(relay_on, HIGH);
  delay(50);
  digitalWrite(relay_on, LOW);
  delay(1000);
  Serial.println("ON");
  
  Steps2Take  =  STEPS_PER_OUTPUT_REVOLUTION / 12;  // Rotate CW 1/12 turn
  small_stepper.setSpeed(100);   
  small_stepper.step(Steps2Take);
  delay(10);
  
  digitalWrite(relay_off, HIGH);
  delay(50);
  digitalWrite(relay_off, LOW);
  Serial.println("OFF");
  delay(10);

  SPI.beginTransaction(SPISettings(6000000, MSBFIRST, SPI_MODE3));
  delay(20);
  DS3234_get(ss, &t);
  DS3234_clear_a1f(ss);
  float dstemp = (DS3234_get_treg(ss));

//data written to SD:
      String dataString = "";
      dataString += t.year;
      dataString += ",";
      dataString += t.mon;
      dataString += ",";
      dataString += t.mday;
      dataString += ",";
      dataString += t.hour;
      dataString += ",";
      dataString += t.min;
      dataString += ",";
      dataString += dstemp;
      delay(50);


       while (!sd.begin(CS,SPI_HALF_SPEED)) {
        
        } // initialises SD card again - for when sd card is removed for data
       
       file.open(newfile, O_WRITE | O_APPEND); //Opens the file
       delay(5);
       file.println(dataString); //prints data string to the file
       delay(5);
       Serial.println(dataString);
       delay(100);
       file.close(); //closes the file
       delay(20);
      attachInterrupt(0, alarm, FALLING); //turns back on alarm
}


//SLEEP LOOP
void gotoSleep(void)
{
   byte adcsra = ADCSRA;          //save the ADC Control and Status Register A
   ADCSRA = 0;  //disable the ADC
   sleep_enable();
   power_spi_disable(); 
   set_sleep_mode(SLEEP_MODE_PWR_DOWN);
   cli();
   //sleep_bod_disable();
   sei();
   sleep_cpu();
   /* wake up here */
   sleep_disable();
   power_spi_enable(); 
   ADCSRA = adcsra;               //restore ADCSRA
}


//ALARM LOOP
void alarm()
{
  detachInterrupt(0);
}
double GetTemp(void)
{
  ADMUX = (_BV(REFS1) | _BV(REFS0) | _BV(MUX3));
  ADCSRA |= _BV(ADEN);  
  delay(20);          
  ADCSRA |= _BV(ADSC);  
  while (bit_is_set(ADCSRA,ADSC));
  wADC = ADCW;
}

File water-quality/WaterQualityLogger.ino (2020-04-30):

// Code developed by Environmental Research Group, Department of Geography, King's College London //
////////////////////////////////////////////////////////////////////////////////////////////////////

/* LIBRARIES */
#include <SPI.h>                  //SPI Communication library
#include <avr/sleep.h>            //low power library
#include <avr/power.h>            //low power library
#include <SoftwareSerial.h>       //Software Serial Communication library
#include "ds3234.h"               //DS3234 RTC library. Available from https://github.com/rodan/ds3234
#include <SdFat.h>                //SD card library. Available from https://github.com/greiman/SdFat


//SERIAL COMMS HOUSEKEEPING (FOR DO PROBE)
#define rx 7    //set rx for SoftwareSerial
#define tx 8    //set tx for SoftwareSerial
SoftwareSerial myserial(rx, tx);
String inputstring = ""; 
String sensorstring = ""; 
boolean input_string_complete = false; 
boolean sensor_string_complete = false; 
float DO;


//SD CARD HOUSEKEEPING
const int CS = 10; 
SdFat sd; 
SdFile file;
char newfile[] = "Multiprobe_data.csv"; 


//RTC HOUSEKEEPING
int ss = 9; 
int AlarmPin = 2; 
unsigned char wakeup_min;
struct ts t; 
uint8_t sleep_period = 1; // the sleep interval in minutes between readings. Currently set to 10 minutes 


//OTHER SENSOR HOUSEKEEPING
int T_power=6;      //Thermistor power pin
int C_power=5;      //Central GND power pin (for EC and pressure sensor)

/* ALARM SUBROUTINE */
void set_alarm(void) {
  // calculate the minute when the next alarm will be triggered 
  wakeup_min = (t.min / sleep_period + 1) * sleep_period; 
  if (wakeup_min > 59) {
    wakeup_min -= 60;
    }

  // flags define what calendar component to be checked against the current time in order 
  // to trigger the alarm - see datasheet 
  // A1M1 (seconds) (0 to enable, 1 to disable) 
  // A1M2 (minutes) (0 to enable, 1 to disable) 
  // A1M3 Chour) (0 to enable, 1 to disable) 
  // A1M4 (day) (0 to enable, 1 to disable) 
  // DY/DT (dayofweek == 1/dayofmonth == 0)
  uint8_t flags [4] = { 0, 1, 1, 1};

  // set Alarm1 
  DS3234_set_a2(ss, wakeup_min, 0, 0, flags);

  // activate Alarm1 
  DS3234_set_creg(ss, DS3234_INTCN | DS3234_A2IE);
  
}



/* SETUP */
void setup() {
  Serial.begin(9600); 
  myserial.begin(9600);
  SPI.beginTransaction(SPISettings(6000000, MSBFIRST, SPI_MODE3)); 
  DS3234_init(ss, DS3234_INTCN); 
  delay(10); 
  DS3234_get(ss, &t); 
  delay(10); 
  set_alarm(); 
  DS3234_clear_a2f(ss); 
  delay(10);
  pinMode (AlarmPin, INPUT); 
  pinMode (T_power, OUTPUT); 
  pinMode (C_power, OUTPUT);
  attachInterrupt(0, alarm, FALLING); // setting the alarm interrupt
  while (!sd.begin(CS, SPI_HALF_SPEED)) {
    }

  //Serial.println("Card Initialised”); //would print to the Arduino screen if connected
  // open the file for write at end like the Native SD library 
  file.open(newfile, O_WRITE | O_CREAT | O_APPEND); 
  file.close();
  
  delay(1000);
  inputstring.reserve(10); 
  sensorstring.reserve(30);
}



/* LOOP */
void loop() {
  
  gotoSleep();                  //instigates sleep. Wakes up within subroutine
  delay(5);     
  
  digitalWrite(C_power, HIGH);  //turns on the pressure and EC sensor
  delay(500);                   //half second delay for results to stabilize
  int C = analogRead(A2);       //measure EC
  int P = analogRead(A1);       //measure pressure
  
  digitalWrite(C_power, LOW);   //turns off the pressure and EC sensor
  
  digitalWrite(T_power, HIGH);  //turns on the thermistor
  delay(100); 
  int T = analogRead(A0);       //measure temperature
  digitalWrite(T_power, LOW);   //turns off the thermistor
  
  //uncalibrated readings:
  float C_V = C*3.3/1024.0; 
  float T_V = T*3.3/1024.0; 
  float P_V = P*3.3/1024.0; 
  float T_R = 10.0/T_V*(3.3-T_V); 
  
  //calibrated readings
  float T_T = 1/(2.772539*pow(10,-3) + 2.50767*pow(10,-4)*log(T_R) + 3.37884*pow(10,-7)*pow(log(T_R),3))-273.15; //calibrated temperature reading
  float P_P = (P_V-1.58)*10000.0;   //calibrated pressure reading
  float C_C = 6182.0*C_V;           //calibrated conductivity reading
  
  myserial.print('r');              //send the string to the Atlas Scientific product
  myserial.print('\r');             //add a <CR> to the end of the string
  delay(1800);                      //first result flushed. Repeat reading
  myserial.print('r');              //send the string to the Atlas Scientific product
  myserial.print('\n');             //add a <CR> to the end of the string
  delay(1800);
  
  DO_reading();                     //Run Atlas Scientific DO reading subroutine
  delay(50);
  SPI.beginTransaction(SPISettings(6000000, MSBFIRST, SPI_MODE3)); //initiate SPI communication
  delay(20);
  DS3234_get(ss, &t); 
  set_alarm();                      //reset the alarm
  DS3234_clear_a2f(ss);
  
  String dataString = ""; 
  dataString += t.year; 
  dataString += ","; 
  dataString += t.mon;
  dataString += ","; 
  dataString += t.mday; 
  dataString += ","; 
  dataString += t.hour;
  dataString += ","; 
  dataString += t.min;
  dataString += ","; 
  dataString += C_V; 
  dataString += ","; 
  dataString += C_C; 
  dataString += ","; 
  dataString += P_V; 
  dataString += ","; 
  dataString += T_T; 
  dataString += ","; 
  dataString += DO;
  
  file.open(newfile, O_WRITE | O_APPEND); //Opens the file 
  delay(5); 
  file.println(dataString); 
  //prints data string to the file 
  delay(5); 
  file.close(); //closes the file 
  delay(5); 
  Serial.println(dataString); 
  delay(100);
  
  attachInterrupt(0, alarm, FALLING);
  
} //end loop


/* SLEEP SUBROUTINE */
void gotoSleep(void) { 
  byte adcsra = ADCSRA;   //save the ADC Control and Status Register 
  ADCSRA = 0;         //disable the ADC 
  sleep_enable(); 
  power_spi_disable(); 
  set_sleep_mode(SLEEP_MODE_PWR_DOWN); 
  cli(); 
  sleep_bod_disable(); 
  sei(); 
  sleep_cpu(); 
  /* wake up here */ 
  sleep_disable(); 
  power_spi_enable(); 
  ADCSRA = adcsra;      //restore ADCSRA
}


/* ALARM SUBROUTINE */
void alarm() {
    detachInterrupt(0);
}


/* ATLAS SCIENTIFIC DO READING SUBROUTINE */
void DO_reading() {
  myserial.print('R');
  myserial.print('\r'); // delay(1800);
  
  while (myserial.available()) {
  char inchar = (char)myserial.read(); 
  //delay(10);
  sensorstring += inchar; 
  
  if (inchar == '\r') { 
    sensor_string_complete = true;
    //Serial.println(sensorstring); //if wanting to print the immediate DO reading
    }
  }

  if (sensor_string_complete== true) {
    if (isdigit(sensorstring[0])) DO = sensorstring.toFloat();
  
    sensorstring = "";
    sensor_string_complete = false;
    myserial.print("Sleep"); 
    myserial.print('\r'); 
    delay(1800);
    }
}

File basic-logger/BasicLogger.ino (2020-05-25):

// Code developed by Environmental Research Group, Department of Geography, King's College London //
////////////////////////////////////////////////////////////////////////////////////////////////////

/* LIBRARIES */
#include <SPI.h>                  //SPI Communication library
#include <avr/sleep.h>            //low power library
#include <avr/power.h>            //low power library
#include "ds3234.h"               //DS3234 RTC library. Available from https://github.com/rodan/ds3234
#include <SdFat.h>                //SD card library. Available from https://github.com/greiman/SdFat

//SD HOUSEKEEPING
  SdFat sd;
  SdFile file;
  char newfile[] = "BasicTemperatureLogger.csv";      //name of file
  const int CS = 10;        //sd card chip select


//RTC & ALARM HOUSEKEEPING
  int ss = 9;               //clock chip select
  int AlarmPin = 2;         //pin which alarm communicates with
  unsigned char wakeup_min;
  struct ts t;
  uint8_t sleep_period = 1;                 //sleep period. Currently set to every minute.
  volatile boolean extInterrupt1 = false;

unsigned int wADC;

/* ALARM SUBROUTINE */
void set_alarm(void){  
    wakeup_min = (t.min / sleep_period + 1) * sleep_period;
    if (wakeup_min > 59) {
        wakeup_min -= 60;
    }
    uint8_t flags[4] = { 0, 1, 1, 1};   
    DS3234_set_a2(ss, wakeup_min, 0, 0, flags);       //set Alarm1
    DS3234_set_creg(ss, DS3234_INTCN | DS3234_A2IE);  //activate Alarm1
}

/* SETUP */
void setup() {
  Serial.begin(9600);
  Serial.println("setupstart");
  SPI.beginTransaction(SPISettings(6000000, MSBFIRST, SPI_MODE3));
  DS3234_init(ss, DS3234_INTCN);  
  delay(10);
  DS3234_get(ss, &t);
  delay(10);
  set_alarm();
  DS3234_clear_a2f(ss);
  delay(10);
  pinMode (AlarmPin, INPUT);
  attachInterrupt(0, alarm, FALLING); // setting the alarm interrupt 
  delay(10);

  while (!sd.begin(CS, SPI_HALF_SPEED)) {}
  // open the file for write at end like the Native SD library
  file.open(newfile, O_WRITE | O_CREAT | O_APPEND);
  file.close();
  Serial.println("setupend"); //would print to the Arduino screen if connected
  delay(100); 
 } //END SETUP

/* LOOP */
void loop() {
Serial.println("Loop begin -> Going to sleep."); //would print to the Arduino screen if connected
  delay(50);
  gotoSleep();              //Arduino put to sleep
  delay(50);
  detachInterrupt(0);       //turns off alarm
  if (extInterrupt1) extInterrupt1 = false;

  //Measure internal ATmega328p temperature
  GetTemp();
  int InternalTemp = wADC;
  
  SPI.beginTransaction(SPISettings(6000000, MSBFIRST, SPI_MODE3));
  delay(20);
  DS3234_get(ss, &t);
  set_alarm();
  DS3234_clear_a2f(ss);
  float dstemp = (DS3234_get_treg(ss)); //get DS3234 temp
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

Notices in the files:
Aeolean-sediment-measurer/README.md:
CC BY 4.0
